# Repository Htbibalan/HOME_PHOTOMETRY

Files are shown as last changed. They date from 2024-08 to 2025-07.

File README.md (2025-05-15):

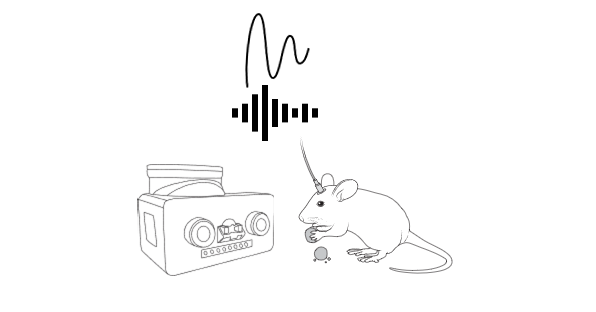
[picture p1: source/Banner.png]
Banner Image


# RTFED_Pi
* RTFED_Pi and associated GUIs is the other version of Clasic ([RTFED](https://github.com/mccutcheonlab/FED_RT/tree/main)) which is an open-source versatile tool for home-cage monitoring of behaviour and fiber photometry recording in mice, this system is developed as a home-cage setup to incorporate [FED3](https://github.com/KravitzLabDevices/FED3/wiki) units with TDT [RZ10](https://www.tdt.com/docs/hardware/rz10-lux-integrated-processor/) photometry system or to capture event-triggered videos of behaviour or to only monitor food intake and other relevant behaviours remotely and online.

# Make sure to flash your FED3 devices with the RTS library provided [here](https://github.com/Htbibalan/FED_RT/tree/main/source/FED3_Library/RTS)

## RbPi Approach
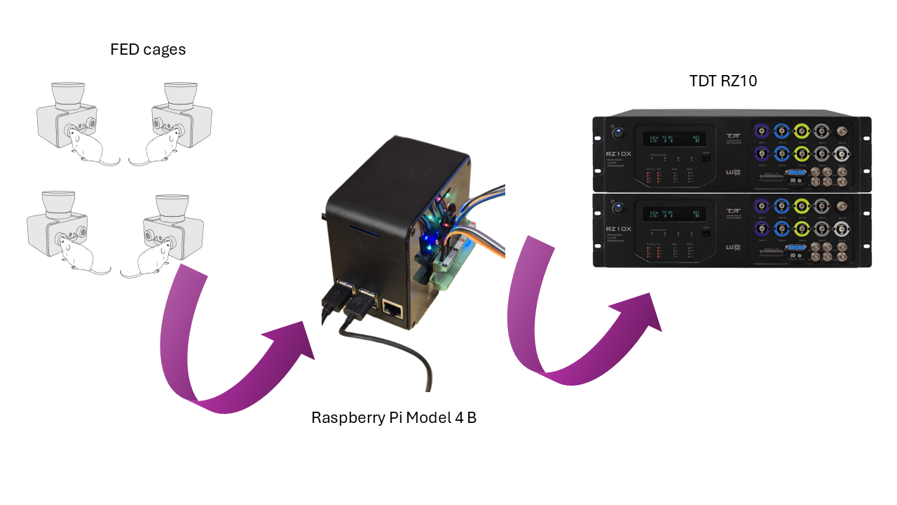
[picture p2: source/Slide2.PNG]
RBPI


RTFED_Pi
RTFED_TOWER

# RTFED(PiOS)
RTFED(PiOS) can be used to remotely monitor the feeding behaviour and other interactions made by mice on FED3, the data is automatically transferred to a Google spreadsheet where you can view it or define alarm notification using the Google Apps Scripts. Using the RTFED you can also change the Mode of your FED3s without the hassle of poking one by one!
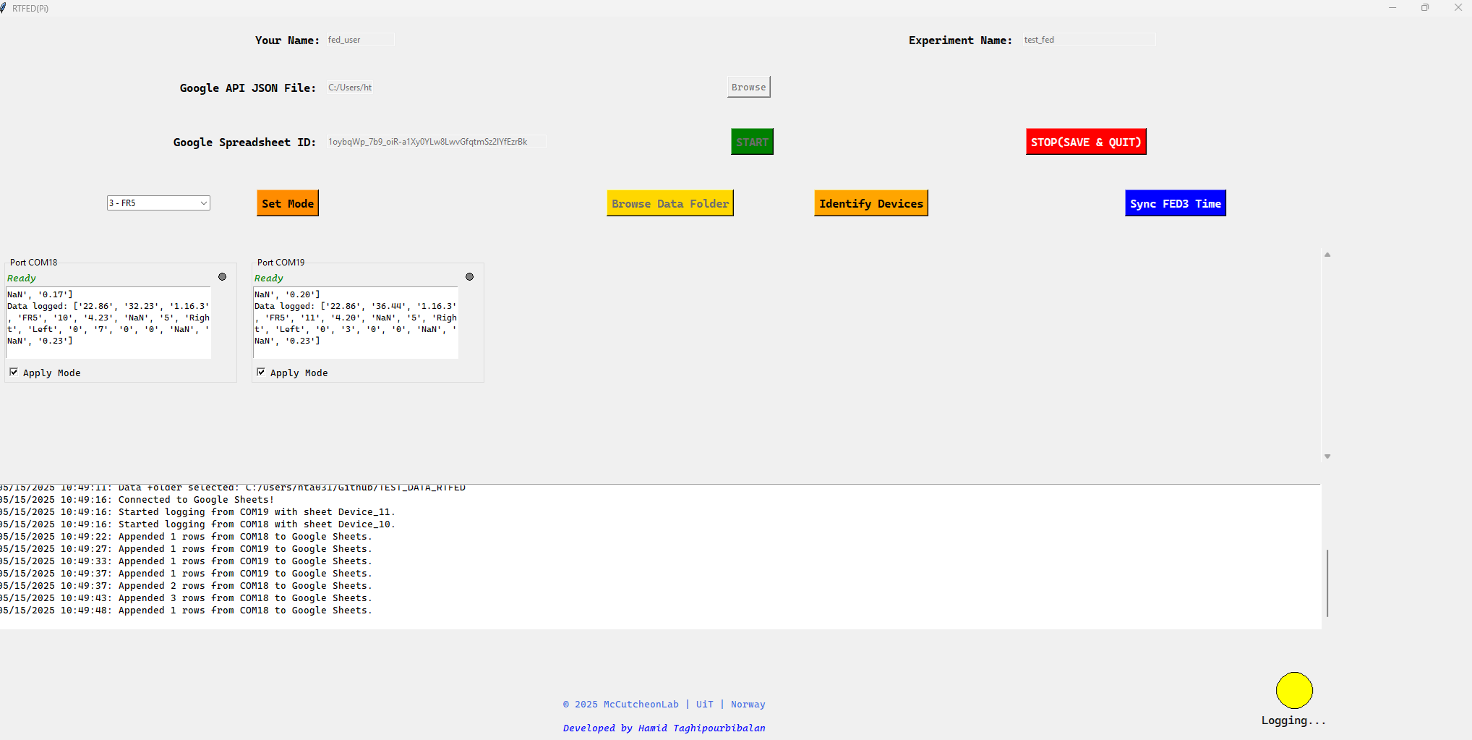
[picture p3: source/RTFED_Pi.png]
RTFED_PiOS


# RTFED(PiCAM)
RTFED(PiCAM) is an additional feature to the basic RTFED where you can enhance your behavioural studies by having event-triggered video recording. Primarily the RTFED(PiCAM) can record videos of mice using common USB cameras after taking Pellets, making Left or Right pokes or a combination of All of these events. Videos are limited to 30 sec length to capture only relevant behaviours while saving storage space, in this configuration, e.g. after taking a pellet, the GUI records the behaviour for 30 sec, if another pellet is taken within this 30 sec, it keeps recording for an extra 30 sec until no more pellet is taken.
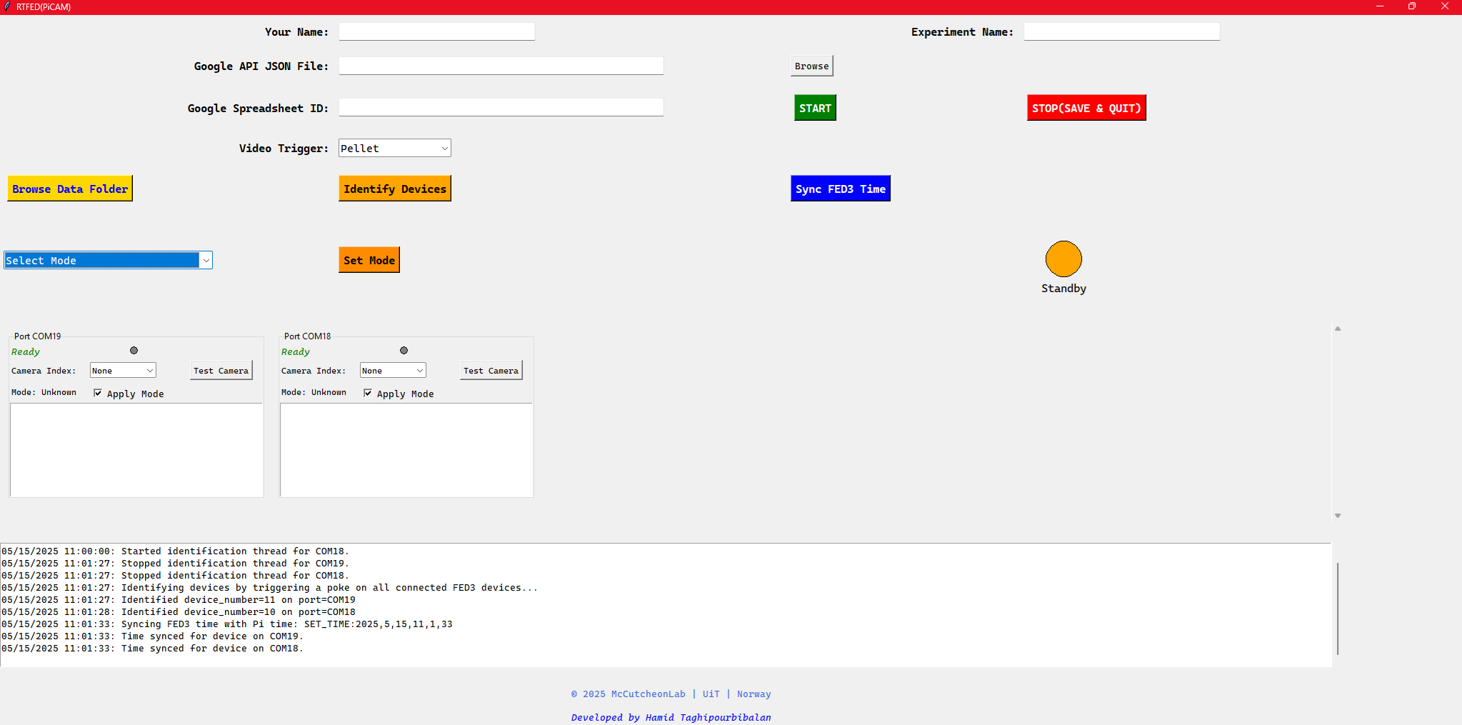
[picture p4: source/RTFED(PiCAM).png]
RTFED_PiCAM


# RTFED(PiTTL)
The TTL station of RTFED logs behavioural events made on FED3 devices and transmit them to the TDT RZ10 processors as TTL pulses. This features enables you to study event-locked signals in your experiments. However the PiTTL version does not send data online to reduce any processing load that might delay the rapid TTL puls transmission.

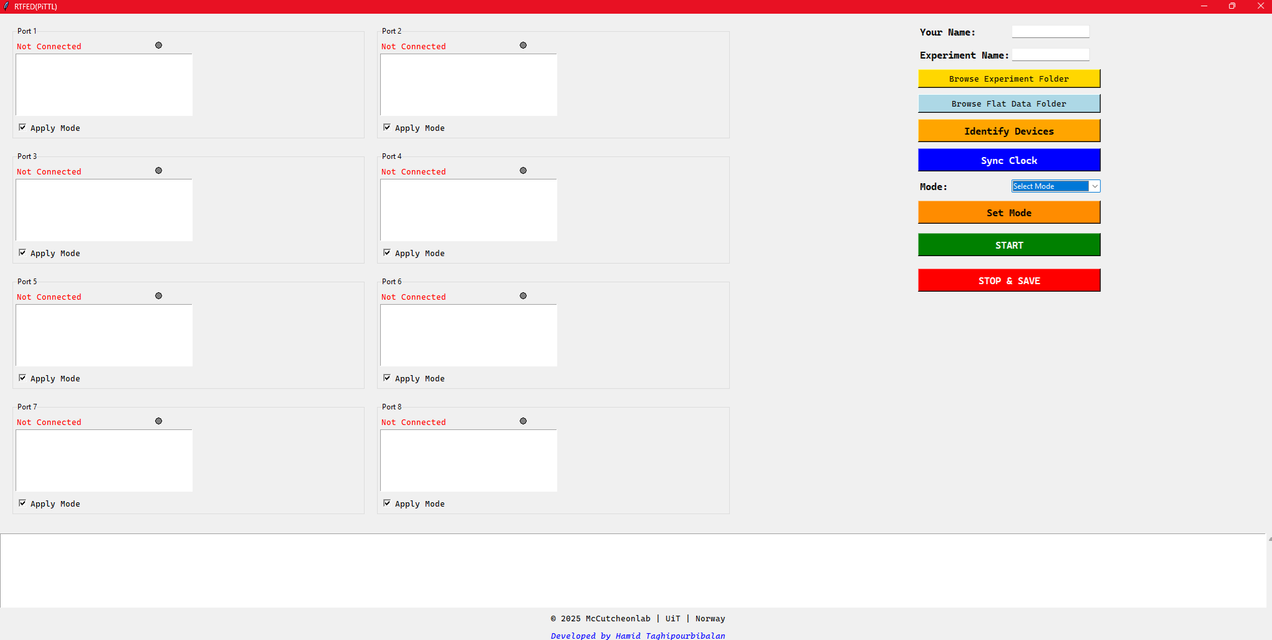
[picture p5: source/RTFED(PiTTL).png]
RTFED_PiTTL


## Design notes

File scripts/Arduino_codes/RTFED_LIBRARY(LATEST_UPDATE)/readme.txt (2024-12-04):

to run RTFED (with or without camera) and the TTL system on raspberry pi, the FEDs should be flashed with these codes

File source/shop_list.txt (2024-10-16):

## The Raspberry Pi 4 Model B - 4 GB RAM
https://www.electrokit.com/en/raspberry-pi-4-model-b/4gb

## A cover case for the board  maybe?(we could 3D print something, but it is already cheap and designing and printing would probably cost more!)
https://www.electrokit.com/en/raspberry-pi-4-inbyggnadslada-rod/vit

## The power adapter for the board
https://www.electrokit.com/en/raspberry-pi-4-stromforsorjning-5v-3a-usb-c-vit

## SD card for the board:
https://www.electrokit.com/en/minneskort-microsdxc-128gb-klass-10-a1

## Jumper wires to connect raspberry pi board to db25 breakoutboard
https://www.elfadistrelec.no/en/jumper-cable-of-40-wires-male-to-female-awg22-velleman-wpa414/p/30260971?ext_cid=shgooaqnono-Shopping-PerformanceMax-CSS&gad_source=1&gclid=CjwKCAjw8rW2BhAgEiwAoRO5rPSryj3k5p8T8V73ak9BMlPEfC4beYDF5v3y66Gtu4eO7EGV2-FF5RoCgv8QAvD_BwE&gclsrc=aw.ds

## DB25 breakout board - connector plug (I am a bit unsure what to choose here)

**Do you think using this one from Amazon makes it easy to map the pins?  - - -instead of using a jumper wire connection to a breakout board and then to TDT.**

#### https://www.amazon.com/JUXINICE-Female-Connector-Provided-Terminals/dp/B0CHNPQBQ8/ref=sr_1_3?crid=2OR78V9CIIFG9&dib=eyJ2IjoiMSJ9.yi8Qg4Rj5wWahTUCXJsKgAnKQk_3SQFYZ_B8QfRRd5V8pHj0V4OxDGAj5KCSfbLMn-YADwfM40hr9cPisJgPzwXafPZrragr_EplipRJSqGdi6IUDoTFnUVk0VAi0_aot9ruiePJBJm4pEvt8D9bhZ1MbMfMwwcu3ZXXE-lrJochcbtGk-mPSx4gX2LDumzK5paAzaQJFuXtPuggM7bJzDdVVN1RYlLLHZg9duVD96s.VZK6kxQxmFYSIs7IfyqwNdEzwP57swXu5cxePmbuzlM&dib_tag=se&keywords=db25%2Bpigtail%2Bfemale%2Bjumper%2Bwire%2Bon%2Bend&qid=1724755007&sprefix=db25%2Bpigtail%2Bfemale%2Bjumper%2Bwire%2Bon%2Ben%2Caps%2C204&sr=8-3&th=1

#### https://czh-labs.com/products/czh-labs-slim-right-angle-dsub-db25-male-header-breakout-board-module-d-sub-231?gad_source=1&gclid=CjwKCAjw8rW2BhAgEiwAoRO5rEic1w67dlyraS9dUXNrp32Dhq9PTFB_XoJzjpuoE9zxFm3M3ATWWRoCE30QAvD_BwE

#### https://www.multicom.no/delock-seriell-adapter-db-25-til/cat-p/c/p5398359?gad_source=1&gclid=CjwKCAjw8rW2BhAgEiwAoRO5rKDj3SsBziStjbM7XgD4G3ZDbnNtTQQtALRzAGIcXfvrEBEA31QwJhoCIz0QAvD_BwE

## micro-USB extension
When mounted, the usb port on feather board of FEDs is very badly accessible,this tiny extension can be plugged in and folded back inside the FED housing -- - so the user can easily plug the USB cable on and off

https://www.amazon.com/Uogw-Micro-USB-Extension-Compatible-Extender/dp/B0CLNST44W/ref=sr_1_12_sspa?crid=2T2GL28DFSUQF&dib=eyJ2IjoiMSJ9.ToT3-_PpHgo8qtZdqoQMA_RmyXm6rntiebAVAt7THINzPbDIxeCftpZySoyK1GaJeZY26zIsTFYda32_0IthTOMxalG1sVhi6l7dpbQTZtIAAegbQhmTqVs8Re8zaWFydS_tD66FhC2EADfzfWHkswVANtIlt0KJgT7VXEkySAhnAKVyMKRxunJ3VUaQDT3ZaAcAWanG9JjlNHgFYxLHJ7A2aLwAGYZ1YsdB2rNlqzk.O1Yd72mzAjQylSQsHVLrKwEAeE-LObh2ErCST5r62MY&dib_tag=se&keywords=micro+usb+extension&qid=1724755350&sprefix=micro+usb+extensio%2Caps%2C215&sr=8-12-spons&sp_csd=d2lkZ2V0TmFtZT1zcF9tdGY&psc=1

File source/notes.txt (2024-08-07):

Andrew Hardaway method to sync FED with photometry
https://hackaday.io/project/106885-feeding-experimentation-device-3-fed3/log/162040-interfacing-fed3-with-bonsai

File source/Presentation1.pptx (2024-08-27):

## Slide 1

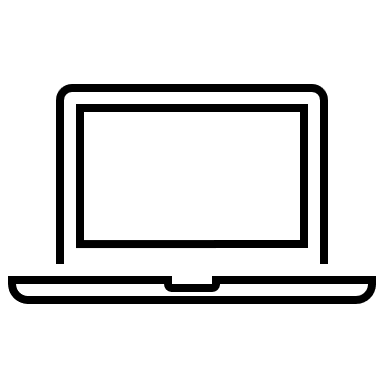
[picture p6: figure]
Laptop outline

Central computer

FED cages

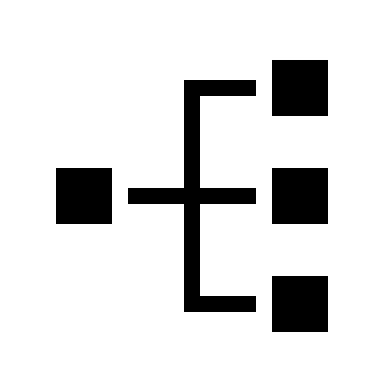
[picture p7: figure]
Network diagram with solid fill
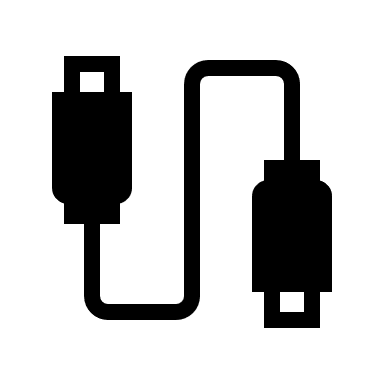
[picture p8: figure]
USB with solid fill
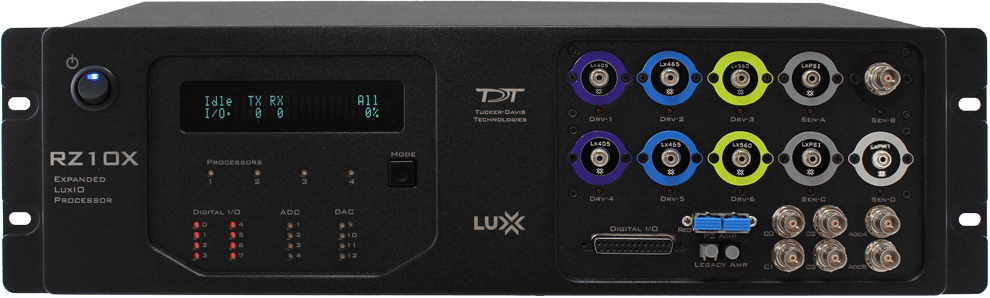
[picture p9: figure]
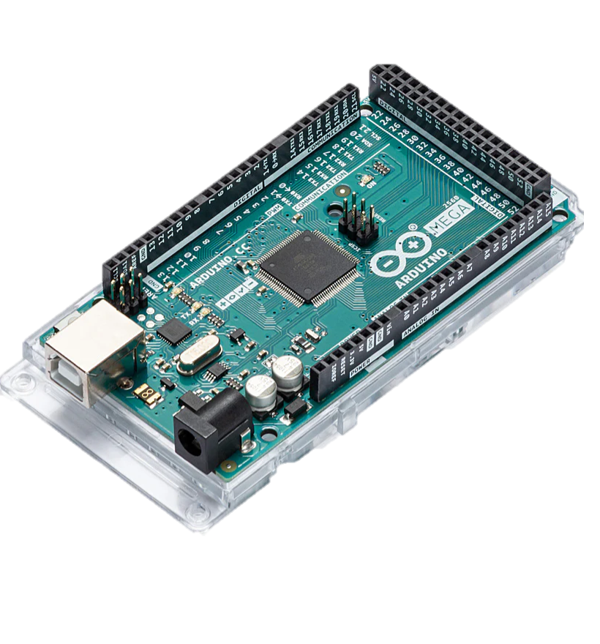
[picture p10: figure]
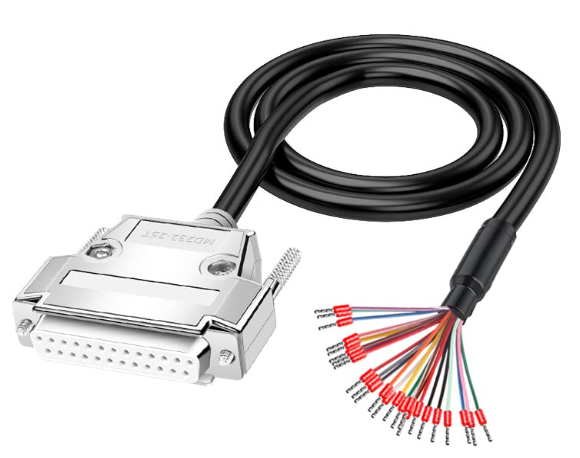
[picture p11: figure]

Arduino Mega

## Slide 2

Raspberry Pi Model 4 B

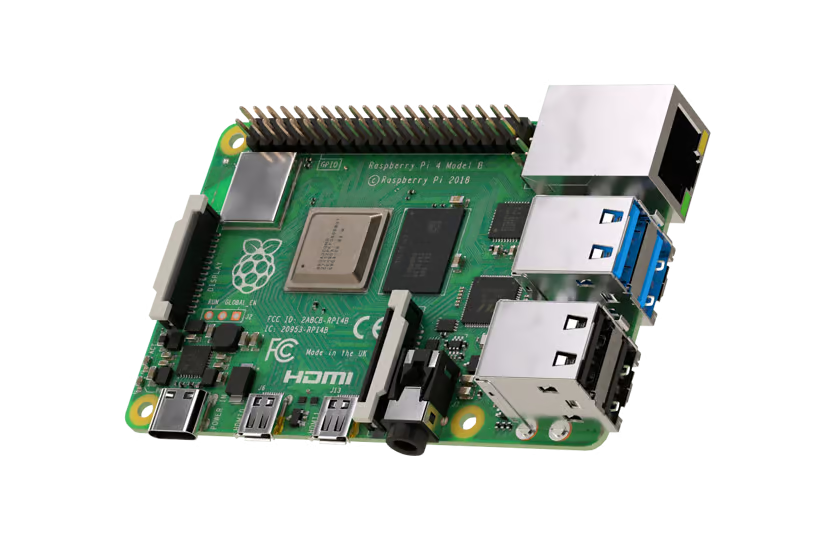
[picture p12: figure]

FED cages

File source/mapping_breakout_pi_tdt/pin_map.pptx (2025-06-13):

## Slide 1

Db25 breakout to TDT

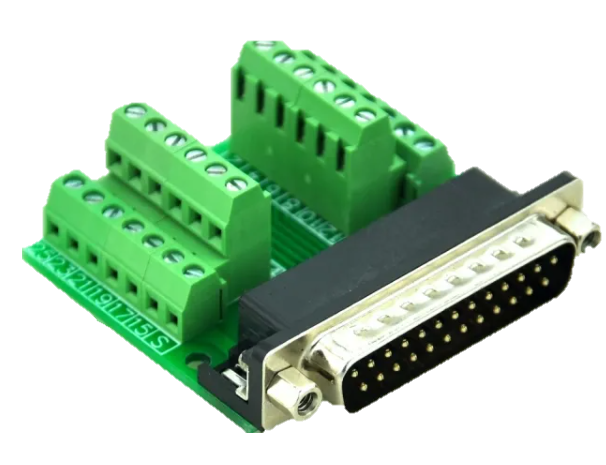
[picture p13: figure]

Port 3/4
Db25 Pin Jumper colour
1 White Right 5
14 Gray Left 0
2 Black Pellet 6
15 Red Right 19
3 Brown Left 13
16 Orange Pellet 26
5 Purple Ground

Raspberry Pi GPIO pinout

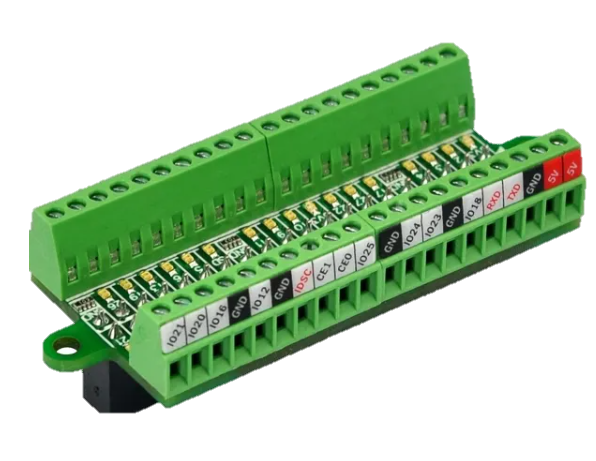
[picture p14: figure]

gpio_pins_per_device = {
'Port 1': {"LeftPoke": 17, "RightPoke": 27, "Pellet": 22},
'Port 2': {"LeftPoke": 10, "RightPoke": 9, "Pellet": 11},
'Port 3': {"LeftPoke": 0, "RightPoke": 5, "Pellet": 6},
'Port 4': {"LeftPoke": 13, "RightPoke": 19, "Pellet": 26},
'Port 5': {"LeftPoke": 14, "RightPoke": 15, "Pellet": 18},
'Port 6': {"LeftPoke": 23, "RightPoke": 24, "Pellet": 25},
'Port 7': {"LeftPoke": 8, "RightPoke": 7, "Pellet": 1},
'Port 8': {"LeftPoke": 12, "RightPoke": 16, "Pellet": 20},
}

Port 1/2
Db25 Pin Jumper colour
1 White Right 27
14 Gray Left 17
2 Black Pellet 22
15 Green Right 9
3 Yellow Left 10
16 Blue Pellet 11
5 Purple Ground

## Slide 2

Raspberry Pi GPIO pinout

gpio_pins_per_device = {
'Port 1': {"LeftPoke": 17, "RightPoke": 27, "Pellet": 22},
'Port 2': {"LeftPoke": 10, "RightPoke": 9, "Pellet": 11},
'Port 3': {"LeftPoke": 0, "RightPoke": 5, "Pellet": 6},
'Port 4': {"LeftPoke": 13, "RightPoke": 19, "Pellet": 26},
'Port 5': {"LeftPoke": 14, "RightPoke": 15, "Pellet": 18},
'Port 6': {"LeftPoke": 23, "RightPoke": 24, "Pellet": 25},
'Port 7': {"LeftPoke": 8, "RightPoke": 7, "Pellet": 1},
'Port 8': {"LeftPoke": 12, "RightPoke": 16, "Pellet": 20},
}

Db25 breakout to TDT

Port 1/2
Db25 Pin Pi pin
1 Right 27
14 Left 17
2 Pellet 22
15 Right 9
3 Left 10
16 Pellet 11
5 Ground

Port 3/4
Db25 Pin Pi pin
1 Right 5
14 Left 0
2 Pellet 6
15 Right 19
3 Left 13
16 Pellet 26
5 Ground

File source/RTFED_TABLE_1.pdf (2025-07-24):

Component | Quantity | Cost/unit (USD) | PiTTL | PiCAM | Basic
Raspberry Pi 4 Model B 4 GB | 1 | 62 | ✓ | ✓
Power supply 15W USB-C | 1 | 9 | ✓ | ✓
Memory card microSD 128 GB Class 10 A1 | 1 | 15 | ✓ | ✓
Raspberry Pi 4 B Tower Case | 1 | 30 | ✓ | ✓
DB25 Male Header Breakout Board | 2 | 12 | ✓
Ultra-small RPi GPIO LED Breakout | 1 | 19 | ✓
Jumper wires Male-Male | 1 | 3.5 | ✓
Arducam 1080P Day/Night Vision USB Camera | As needed | 34 | | ✓
USB Camera mount | As needed | – | | ✓
Powered USB hub | As needed | 20 | ✓ | ✓ | ✓
Long USB-A to Micro-B cables | As needed | 7.5 | ✓ | ✓ | ✓
MicroHDMI cable | 1 | 8 | ✓ | ✓
Bluetooth keyboard-touchpad | 1 | 40 | ✓ | ✓
Optional: DB25 extension cable | 2 | 30 | ✓
FED3 (Fully assembled) | As needed | 475 | ✓ | ✓ | ✓

1

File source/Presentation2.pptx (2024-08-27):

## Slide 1

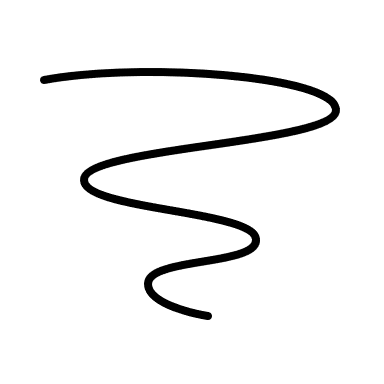
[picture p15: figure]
Squiggle outline
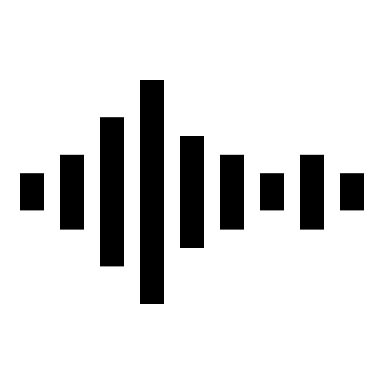
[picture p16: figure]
Voice with solid fill
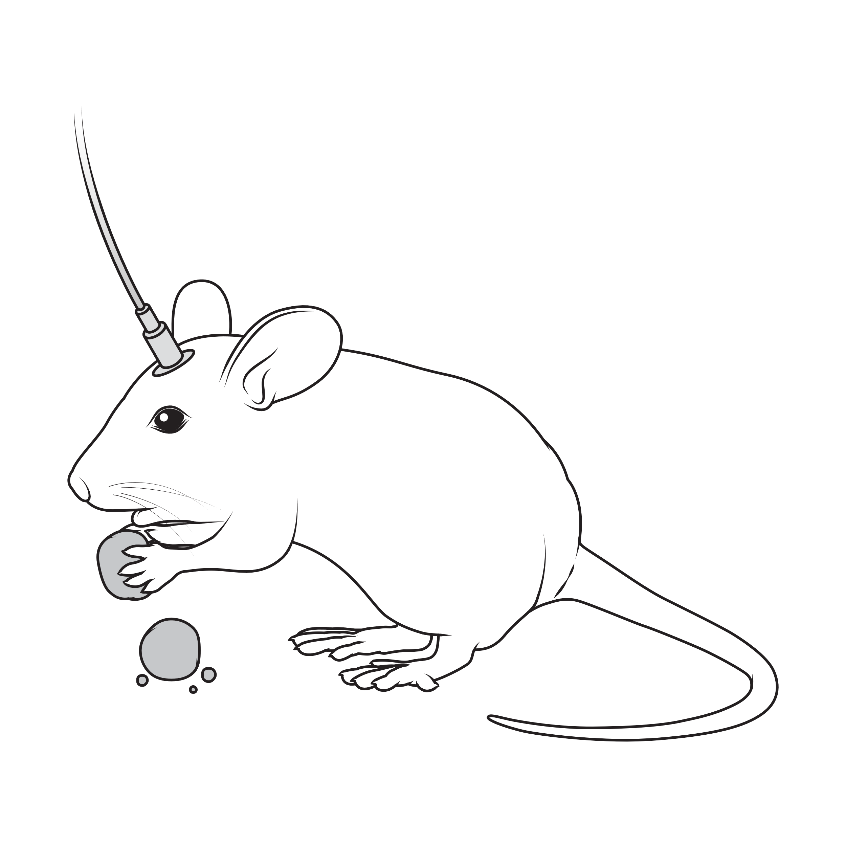
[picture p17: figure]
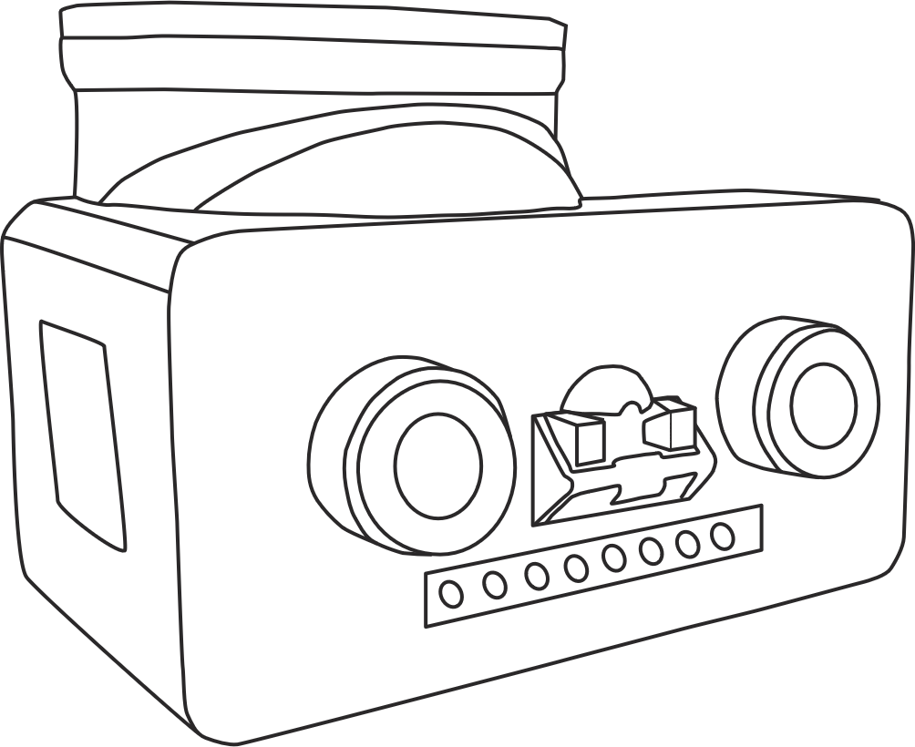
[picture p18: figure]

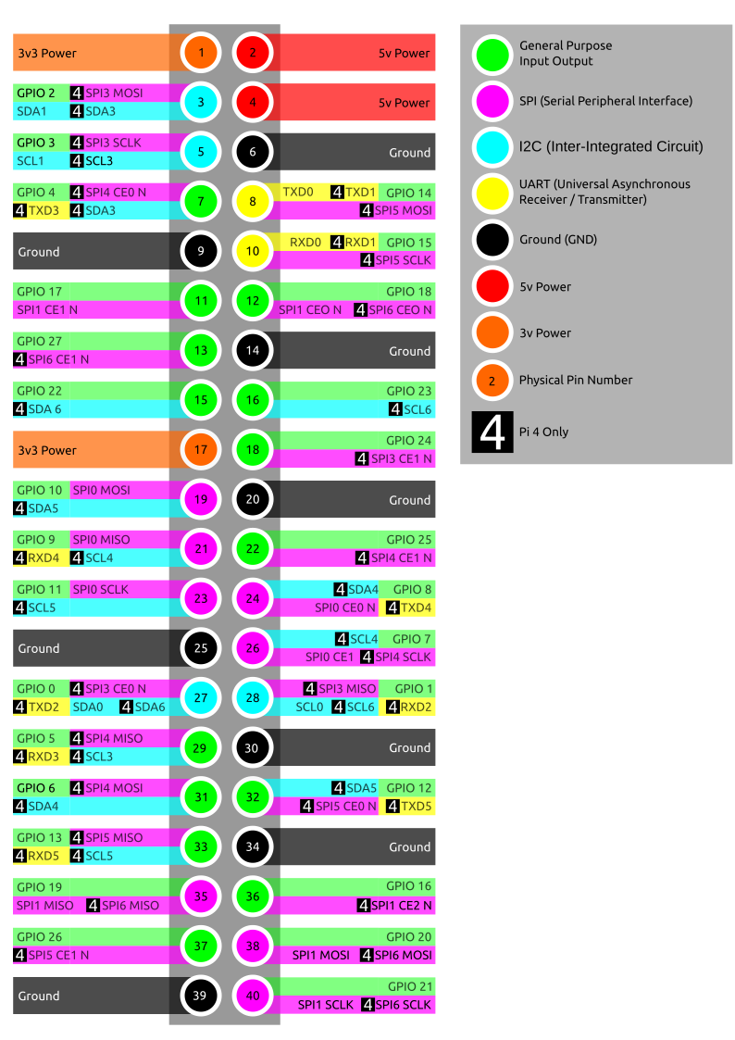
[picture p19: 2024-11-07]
source/PINOUT_rbpi4.png

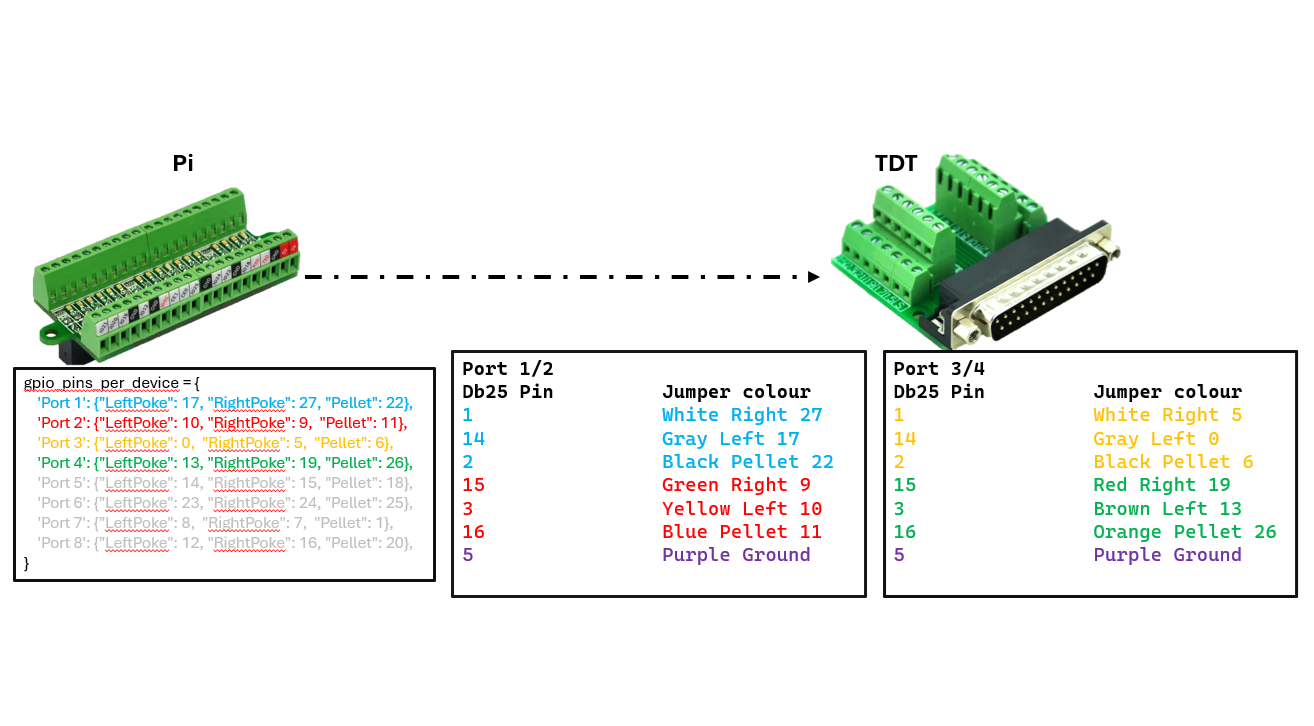
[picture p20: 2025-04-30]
source/mapping_breakout_pi_tdt/pin_map.png

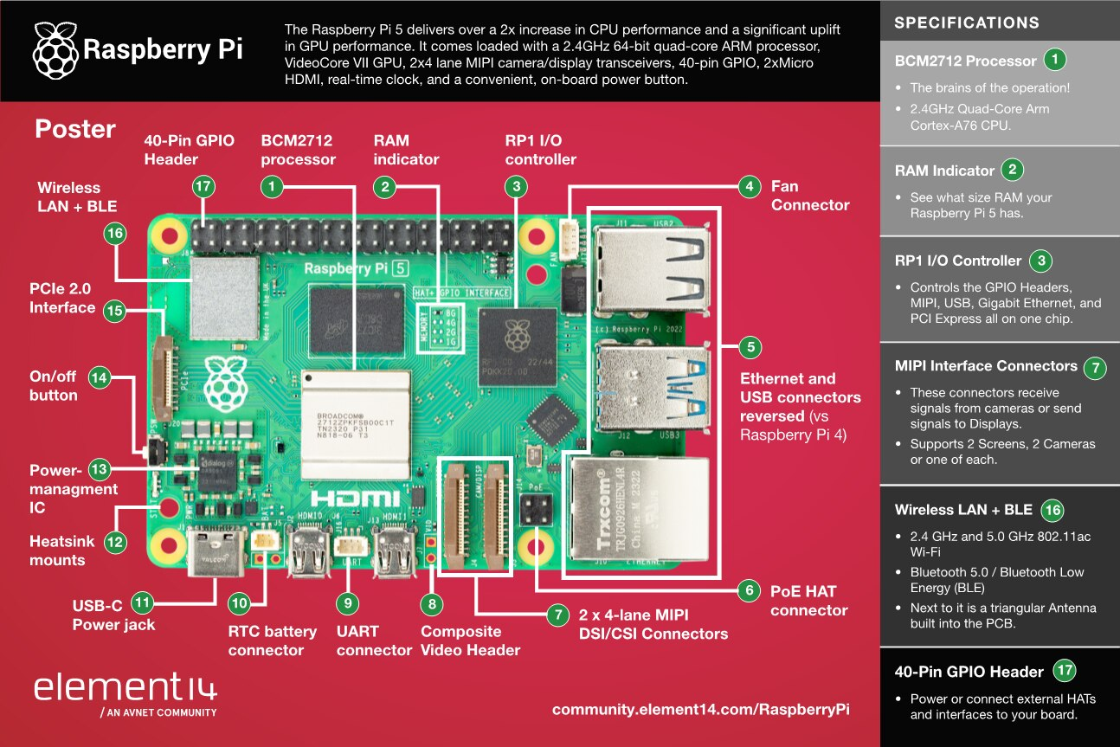
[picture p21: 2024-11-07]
source/otep3xr6.png

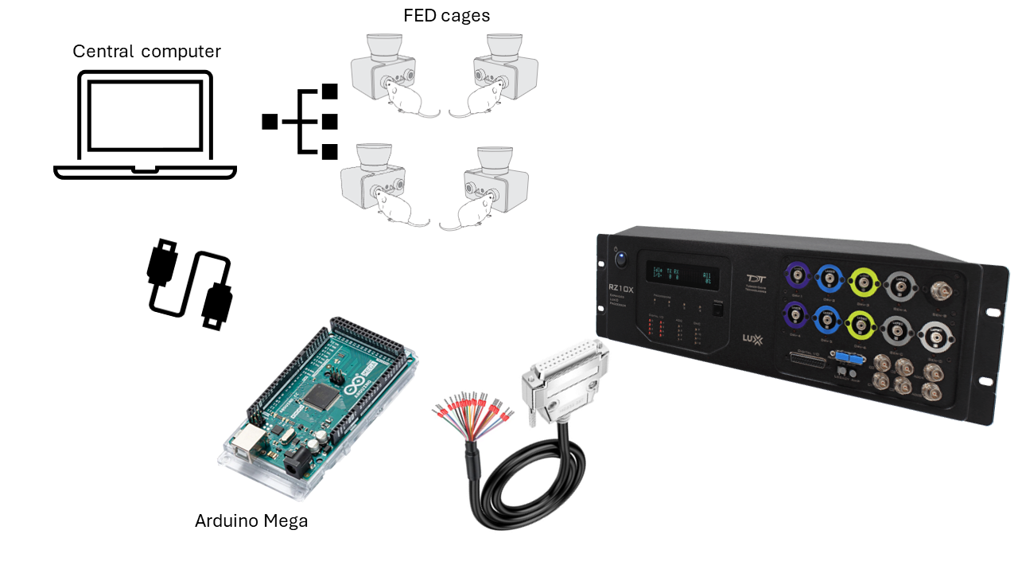
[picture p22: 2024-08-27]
source/Slide1.PNG

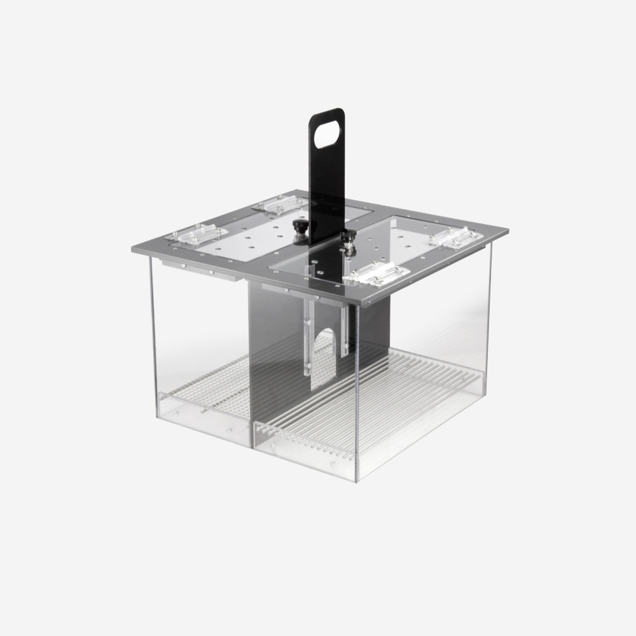
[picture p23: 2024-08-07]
source/hinge_medbox.jpg

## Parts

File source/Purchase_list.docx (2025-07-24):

Component | Quantity | ~ Cost/unit (USD) | Suggested source | Comments
Raspberry Pi 4 Model B 4 GB | 1 | 62 | Amazon (https://www.amazon.com/Raspberry-Pi-RPI4-MODBP-4GB-Model-4GB/dp/B09TTNF8BT) | Only for photometry and video recording
Power supply 15W USB-C | 1 | 9 | Amazon (https://www.amazon.com/Raspberry-Supply-iUniker-Switch-Listed/dp/B097P2NLVH) | Only for photometry and video recording
Memory card microSD 128 GB Class 10 A 1 | 1 | 15 | Amazon (https://www.amazon.com/SanDisk-128GB-microSDXC-Memory-Adapter/dp/B0B7NTY2S6) | Only for photometry and video recording
Raspberry Pi 4 B Tower Case | 1 | 30 | Amazon (https://www.amazon.com/ElectroCookie-Raspberry-Aluminum-Cooling-Changing/dp/B09QG349ZL) | Only for photometry and video recording
DB25 Male Header Breakout Board | 2 | 12 | CZH-LABS (https://czh-labs.com/products/czh-labs-slim-right-angle-dsub-db25-male-header-breakout-board-module-d-sub-231) | Only for photometry
Ultra-small RPi GPIO Status LED & Terminal Block Breakout Board | 1 | 19 | CZH-LABS (https://czh-labs.com/products/ultra-small-rpi-gpio-status-led-terminal-block-breakout-board-module-for-raspberry-pi) | Only for photometry
Jumper wires Male-Male | 1 | 3.5 | Arduino (https://store-usa.arduino.cc/products/40-colored-male-male-jumper-wires) | Only for photometry
Arducam 1080P Day/Night Vision USB Camera | As needed | 34 | ArduCam (https://www.arducam.com/arducam-1080p-day-night-vision-usb-camera-2mp-infrared-webcam-with-automatic-ir-cut-switching-and-ir-leds.html) | If video recording needed
USB Camera mount | As needed | - | TinkerCAD (https://www.tinkercad.com/things/21BWhLxcOKk-cameramount) | If video recording needed
Powered USB hub | 1 | 20 | Amazon (https://www.amazon.com/FEMORO-Charging-Splitter-Individual-Switches/dp/B0CG8YR4W7) | For more than 4 FEDs
Long USB-A to Micro-B cables | As needed | 7.5 | Amazon (https://www.amazon.com/dp/B07232M876/ref=twister_B072FHJVT2?_encoding=UTF8&th=1)
MicroHDMI cable | 1 | 8 | Amazon (https://www.amazon.com/oldboytech-Adapter-Compatible-Raspberry-Capture/dp/B08C2PVP7J?sp_csd=d2lkZ2V0TmFtZT1zcF9hdGY) | Only for photometry and video recording
Bluetooth keyboard-touchpad | 1 | 40 | Amazon (https://www.amazon.com/Arteck-Universal-7-Colors-Bluetooth-TV-Connected/dp/B09KLPJQPD?sp_csd=d2lkZ2V0TmFtZT1zcF9hdGY) | Only for photometry and video recording
Optional: Male to Female db25 extension cable | 2 | | | Only for photometry
FED3

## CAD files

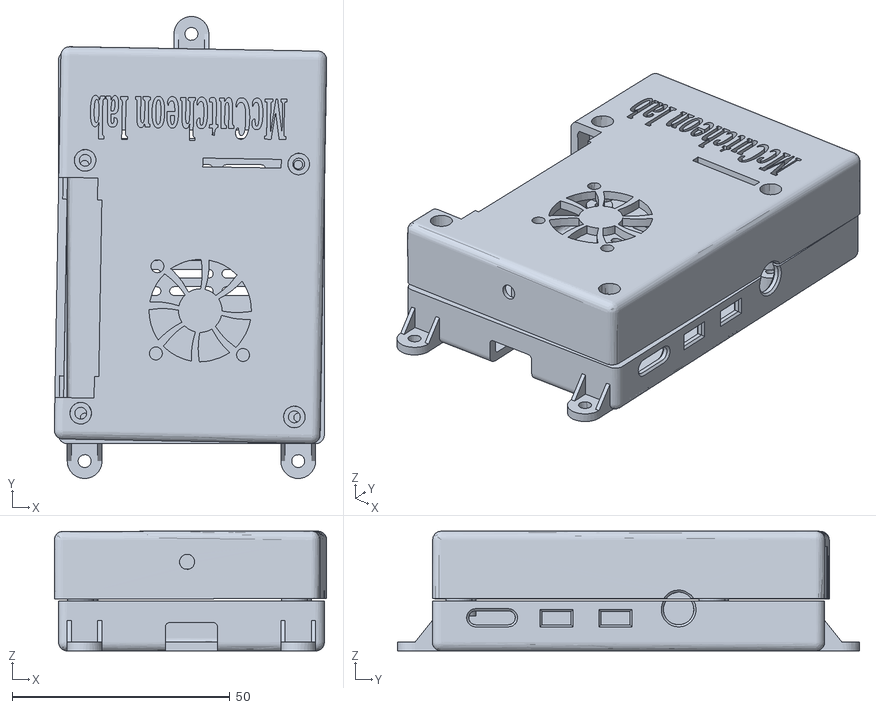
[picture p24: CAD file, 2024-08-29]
source/3D_Model_RbPi/V2/RbPi_V1_whole.stl
62.5 x 106.0 x 27.5

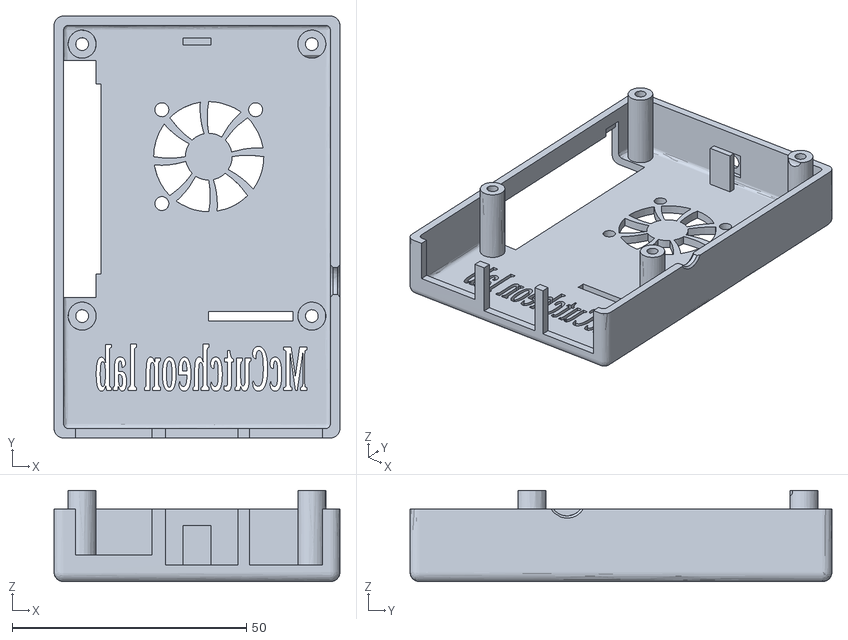
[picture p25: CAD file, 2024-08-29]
source/3D_Model_RbPi/V2/RbPI_V3_Front.stl
61.0 x 90.0 x 19.4

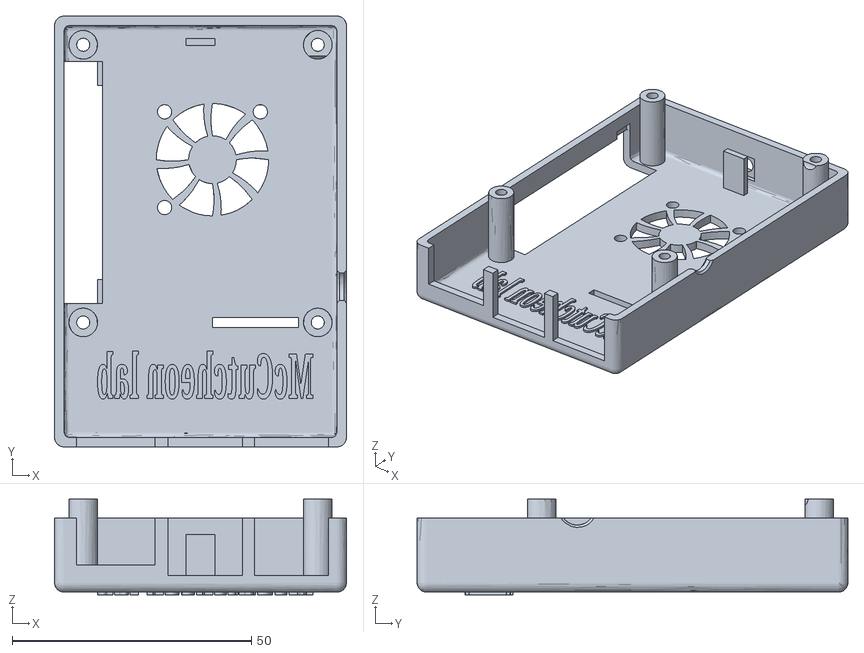
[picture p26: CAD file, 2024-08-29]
source/3D_Model_RbPi/V2/RbPI_V2_Front.stl
61.0 x 90.0 x 20.0

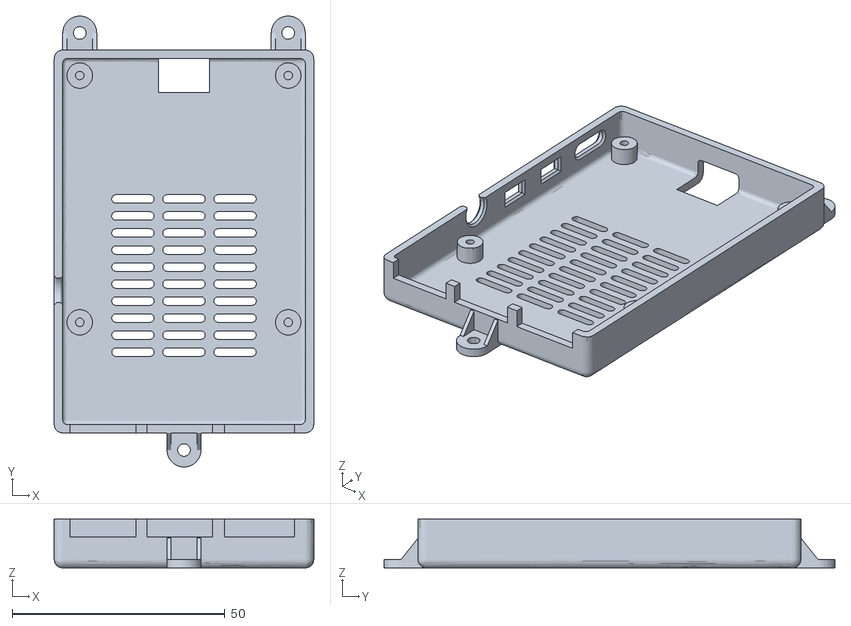
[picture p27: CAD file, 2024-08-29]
source/3D_Model_RbPi/V2/RbPi_V3_Back.stl
61.0 x 106.0 x 11.5

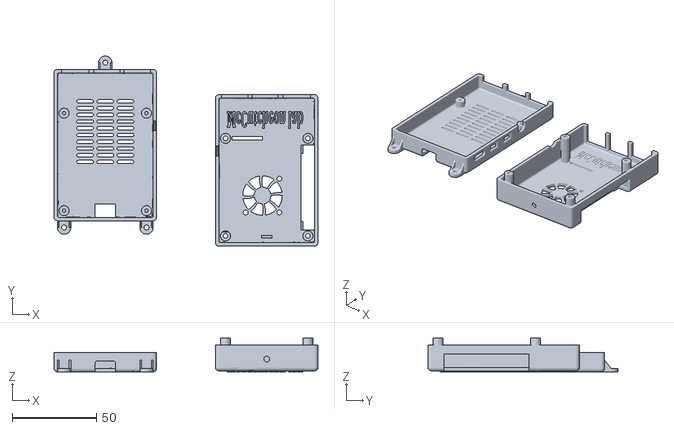
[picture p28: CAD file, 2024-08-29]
source/3D_Model_RbPi/V2/RbPi_V2.stl
157.0 x 113.0 x 20.0

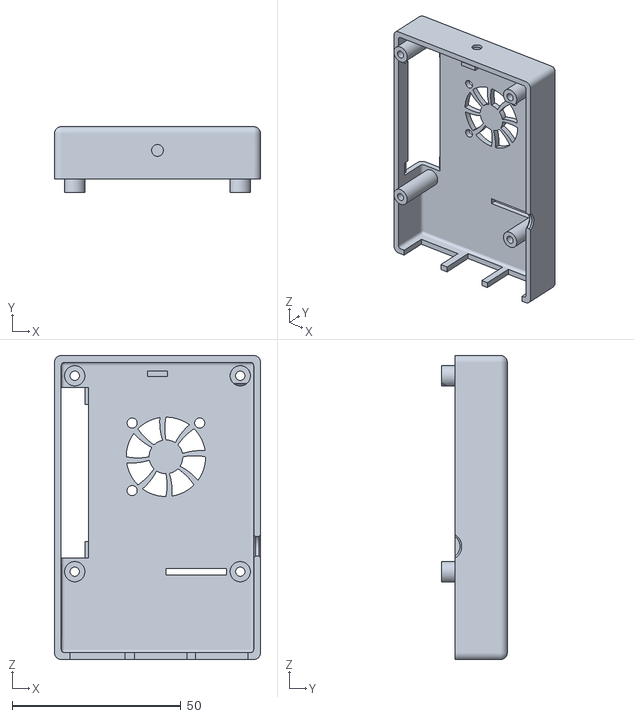
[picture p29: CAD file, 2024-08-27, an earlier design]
source/3D_Model_RbPi/V1/top_V1.stl
61.0 x 19.4 x 90.0

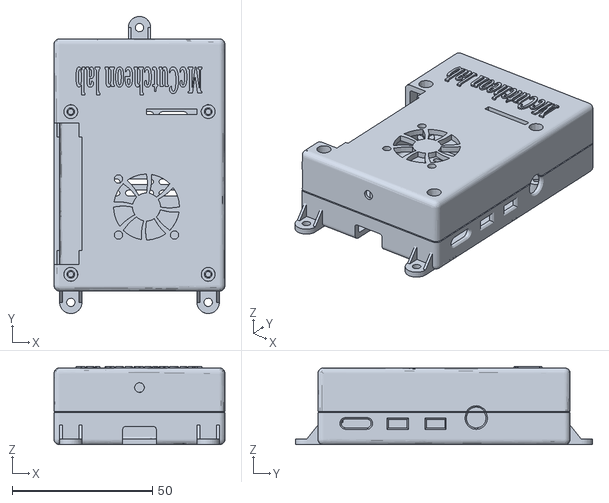
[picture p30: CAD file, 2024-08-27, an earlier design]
source/3D_Model_RbPi/V1/RbPi_V1.stl
61.0 x 106.0 x 28.0

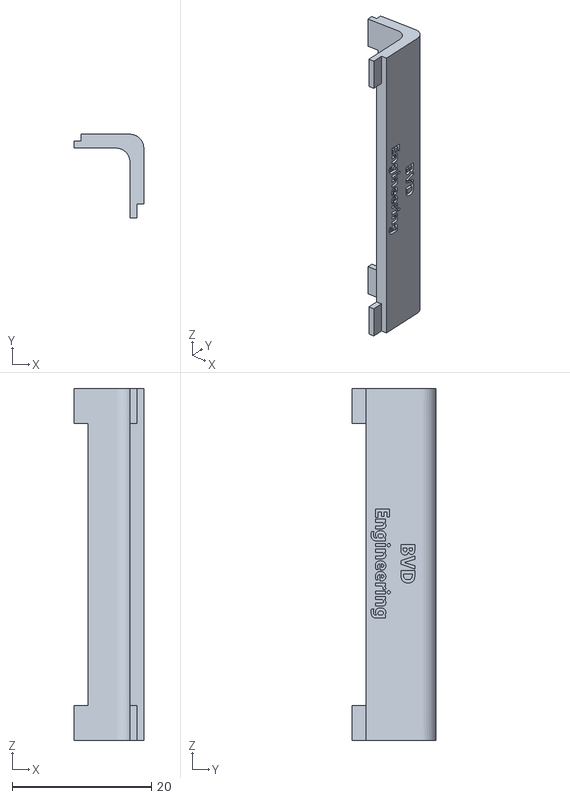
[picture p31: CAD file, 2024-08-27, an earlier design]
source/3D_Model_RbPi/V1/cover_V1.stl
10.0 x 12.0 x 50.5

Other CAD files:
source/3D_Model_RbPi/V1/bottom_V1.stl

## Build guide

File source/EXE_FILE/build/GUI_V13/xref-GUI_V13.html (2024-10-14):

# modulegraph cross reference for GUI_V13.py, pyi_rth__tkinter.py, pyi_rth_inspect.py

GUI_V13.py Script

imports: RPi.GPIO • _collections_abc • _weakrefset • abc • codecs • collections • collections.abc • copyreg • csv • datetime • encodings • encodings.aliases • encodings.ascii • encodings.base64_codec • encodings.big5 • encodings.big5hkscs • encodings.bz2_codec • encodings.charmap • encodings.cp037 • encodings.cp1006 • encodings.cp1026 • encodings.cp1125 • encodings.cp1140 • encodings.cp1250 • encodings.cp1251 • encodings.cp1252 • encodings.cp1253 • encodings.cp1254 • encodings.cp1255 • encodings.cp1256 • encodings.cp1257 • encodings.cp1258 • encodings.cp273 • encodings.cp424 • encodings.cp437 • encodings.cp500 • encodings.cp720 • encodings.cp737 • encodings.cp775 • encodings.cp850 • encodings.cp852 • encodings.cp855 • encodings.cp856 • encodings.cp857 • encodings.cp858 • encodings.cp860 • encodings.cp861 • encodings.cp862 • encodings.cp863 • encodings.cp864 • encodings.cp865 • encodings.cp866 • encodings.cp869 • encodings.cp874 • encodings.cp875 • encodings.cp932 • encodings.cp949 • encodings.cp950 • encodings.euc_jis_2004 • encodings.euc_jisx0213 • encodings.euc_jp • encodings.euc_kr • encodings.gb18030 • encodings.gb2312 • encodings.gbk • encodings.hex_codec • encodings.hp_roman8 • encodings.hz • encodings.idna • encodings.iso2022_jp • encodings.iso2022_jp_1 • encodings.iso2022_jp_2 • encodings.iso2022_jp_2004 • encodings.iso2022_jp_3 • encodings.iso2022_jp_ext • encodings.iso2022_kr • encodings.iso8859_1 • encodings.iso8859_10 • encodings.iso8859_11 • encodings.iso8859_13 • encodings.iso8859_14 • encodings.iso8859_15 • encodings.iso8859_16 • encodings.iso8859_2 • encodings.iso8859_3 • encodings.iso8859_4 • encodings.iso8859_5 • encodings.iso8859_6 • encodings.iso8859_7 • encodings.iso8859_8 • encodings.iso8859_9 • encodings.johab • encodings.koi8_r • encodings.koi8_t • encodings.koi8_u • encodings.kz1048 • encodings.latin_1 • encodings.mac_arabic • encodings.mac_croatian • encodings.mac_cyrillic • encodings.mac_farsi • encodings.mac_greek • encodings.mac_iceland • encodings.mac_latin2 • encodings.mac_roman • encodings.mac_romanian • encodings.mac_turkish • encodings.mbcs • encodings.oem • encodings.palmos • encodings.ptcp154 • encodings.punycode • encodings.quopri_codec • encodings.raw_unicode_escape • encodings.rot_13 • encodings.shift_jis • encodings.shift_jis_2004 • encodings.shift_jisx0213 • encodings.tis_620 • encodings.undefined • encodings.unicode_escape • encodings.utf_16 • encodings.utf_16_be • encodings.utf_16_le • encodings.utf_32 • encodings.utf_32_be • encodings.utf_32_le • encodings.utf_7 • encodings.utf_8 • encodings.utf_8_sig • encodings.uu_codec • encodings.zlib_codec • enum • functools • genericpath • heapq • io • keyword • linecache • locale • logging • ntpath • operator • os • posixpath • pyi_rth__tkinter.py • pyi_rth_inspect.py • queue • re • re._casefix • re._compiler • re._constants • re._parser • reprlib • serial • sre_compile • sre_constants • sre_parse • stat • sys • threading • time • tkinter • tkinter.filedialog • tkinter.font • tkinter.ttk • traceback • types • warnings • weakref

pyi_rth__tkinter.py Script

imports: os • sys

imported by: GUI_V13.py

pyi_rth_inspect.py Script

imports: inspect • os • sys

imported by: GUI_V13.py

'System.IO' MissingModule

imported by: serial.serialcli

'org.python' MissingModule

imported by: copy

RPi Package

imported by: RPi.GPIO • RPi._GPIO

RPi.GPIO Package

imports: RPi • RPi._GPIO

imported by: GUI_V13.py

RPi._GPIO /home/hpfed/HOMEPHOTOFED/lib/python3.11/site-packages/RPi/_GPIO.cpython-311-aarch64-linux-gnu.so

imports: RPi

imported by: RPi.GPIO

System MissingModule

imported by: serial.serialcli

__future__ SourceModule

imported by: serial • serial.serialcli • serial.serialjava • serial.serialposix • serial.serialutil • serial.serialwin32 • serial.win32

_abc (builtin module)

imported by: abc

_ast (builtin module)

imported by: ast

_bisect (builtin module)

imported by: bisect

_blake2 (builtin module)

imported by: hashlib

_bz2 /usr/lib/python3.11/lib-dynload/_bz2.cpython-311-aarch64-linux-gnu.so

imported by: bz2

_codecs (builtin module)

imported by: codecs

_codecs_cn /usr/lib/python3.11/lib-dynload/_codecs_cn.cpython-311-aarch64-linux-gnu.so

imported by: encodings.gb18030 • encodings.gb2312 • encodings.gbk • encodings.hz

_codecs_hk /usr/lib/python3.11/lib-dynload/_codecs_hk.cpython-311-aarch64-linux-gnu.so

imported by: encodings.big5hkscs

_codecs_iso2022 /usr/lib/python3.11/lib-dynload/_codecs_iso2022.cpython-311-aarch64-linux-gnu.so

imported by: encodings.iso2022_jp • encodings.iso2022_jp_1 • encodings.iso2022_jp_2 • encodings.iso2022_jp_2004 • encodings.iso2022_jp_3 • encodings.iso2022_jp_ext • encodings.iso2022_kr

_codecs_jp /usr/lib/python3.11/lib-dynload/_codecs_jp.cpython-311-aarch64-linux-gnu.so

imported by: encodings.cp932 • encodings.euc_jis_2004 • encodings.euc_jisx0213 • encodings.euc_jp • encodings.shift_jis • encodings.shift_jis_2004 • encodings.shift_jisx0213

_codecs_kr /usr/lib/python3.11/lib-dynload/_codecs_kr.cpython-311-aarch64-linux-gnu.so

imported by: encodings.cp949 • encodings.euc_kr • encodings.johab

_codecs_tw /usr/lib/python3.11/lib-dynload/_codecs_tw.cpython-311-aarch64-linux-gnu.so

imported by: encodings.big5 • encodings.cp950

_collections (builtin module)

imported by: collections • threading

_collections_abc SourceModule

imports: abc • sys

imported by: GUI_V13.py • collections • collections.abc • contextlib • locale • os • pathlib • random • types • weakref

_compat_pickle SourceModule

imported by: _pickle • pickle

_compression SourceModule

imports: io • sys

imported by: bz2 • gzip • lzma

_contextvars /usr/lib/python3.11/lib-dynload/_contextvars.cpython-311-aarch64-linux-gnu.so

imported by: contextvars

_csv (builtin module)

imported by: csv

_ctypes /usr/lib/python3.11/lib-dynload/_ctypes.cpython-311-aarch64-linux-gnu.so

imported by: ctypes

_datetime (builtin module)

imports: _strptime • time

imported by: datetime

_decimal /usr/lib/python3.11/lib-dynload/_decimal.cpython-311-aarch64-linux-gnu.so

imported by: decimal

_frozen_importlib ExcludedModule

imported by: importlib • importlib.abc

_frozen_importlib_external MissingModule

imported by: importlib • importlib._bootstrap • importlib.abc

_functools (builtin module)

imported by: functools

_hashlib /usr/lib/python3.11/lib-dynload/_hashlib.cpython-311-aarch64-linux-gnu.so

imported by: hashlib

_heapq (builtin module)

imported by: heapq

_imp (builtin module)

imported by: importlib • importlib._bootstrap_external • importlib.util

_io (builtin module)

imported by: importlib._bootstrap_external • io

_locale (builtin module)

imported by: locale

_lzma /usr/lib/python3.11/lib-dynload/_lzma.cpython-311-aarch64-linux-gnu.so

imported by: lzma

_md5 (builtin module)

imported by: hashlib

_multibytecodec /usr/lib/python3.11/lib-dynload/_multibytecodec.cpython-311-aarch64-linux-gnu.so

imported by: encodings.big5 • encodings.big5hkscs • encodings.cp932 • encodings.cp949 • encodings.cp950 • encodings.euc_jis_2004 • encodings.euc_jisx0213 • encodings.euc_jp • encodings.euc_kr • encodings.gb18030 • encodings.gb2312 • encodings.gbk • encodings.hz • encodings.iso2022_jp • encodings.iso2022_jp_1 • encodings.iso2022_jp_2 • encodings.iso2022_jp_2004 • encodings.iso2022_jp_3 • encodings.iso2022_jp_ext • encodings.iso2022_kr • encodings.johab • encodings.shift_jis • encodings.shift_jis_2004 • encodings.shift_jisx0213

_opcode (builtin module)

imported by: opcode

_operator (builtin module)

imported by: operator

_pickle (builtin module)

imports: _compat_pickle • codecs • copyreg

imported by: pickle

_posixsubprocess (builtin module)

imports: gc

imported by: subprocess

_py_abc SourceModule

imports: _weakrefset

imported by: abc

_pydecimal SourceModule

imports: collections • contextvars • itertools • locale • math • numbers • re • sys

imported by: decimal

_queue /usr/lib/python3.11/lib-dynload/_queue.cpython-311-aarch64-linux-gnu.so

imported by: queue

_random (builtin module)

imported by: random

_sha1 (builtin module)

imported by: hashlib

_sha256 (builtin module)

imported by: hashlib

_sha3 (builtin module)

imported by: hashlib

_sha512 (builtin module)

imported by: hashlib • random

_signal (builtin module)

imported by: signal

_socket (builtin module)

imported by: socket

_sre (builtin module)

imports: copy • re

imported by: re._compiler • re._constants

_stat (builtin module)

imported by: stat

_statistics (builtin module)

imported by: statistics

_string (builtin module)

imported by: string

_strptime SourceModule

imports: _thread • calendar • datetime • locale • re • time

imported by: _datetime • datetime • time

_struct (builtin module)

imported by: struct

_thread (builtin module)

imported by: _strptime • dataclasses • functools • reprlib • tempfile • threading

_threading_local SourceModule

imports: contextlib • threading • weakref

imported by: threading

_tkinter /usr/lib/python3.11/lib-dynload/_tkinter.cpython-311-aarch64-linux-gnu.so

imported by: tkinter

_tokenize (builtin module)

imported by: tokenize

_tracemalloc (builtin module)

imported by: tracemalloc

_typing /usr/lib/python3.11/lib-dynload/_typing.cpython-311-aarch64-linux-gnu.so

imported by: typing

_warnings (builtin module)

imported by: importlib._bootstrap_external • warnings

_weakref (builtin module)

imported by: _weakrefset • collections • weakref

_weakrefset SourceModule

imports: _weakref • types

imported by: GUI_V13.py • _py_abc • threading • weakref

_winapi MissingModule

imported by: encodings • ntpath • subprocess

abc SourceModule

imports: _abc • _py_abc

imported by: GUI_V13.py • _collections_abc • contextlib • dataclasses • email._policybase • functools • importlib._abc • importlib.abc • importlib.metadata • importlib.resources.abc • inspect • io • numbers • os • selectors • typing

argparse SourceModule

imports: copy • gettext • os • re • shutil • sys • textwrap • warnings

imported by: ast • calendar • dis • gzip • inspect • py_compile • tarfile • tokenize • zipfile

array (builtin module)

imported by: serial.serialposix • serial.serialutil • socket

ast SourceModule

imports: _ast • argparse • collections • contextlib • enum • inspect • sys • warnings

imported by: inspect • traceback

atexit (builtin module)

imported by: logging • weakref

base64 SourceModule

imports: binascii • getopt • re • struct • sys

imported by: email._encoded_words • email.base64mime • email.encoders • encodings.base64_codec

binascii (builtin module)

imported by: base64 • email._encoded_words • email.base64mime • email.contentmanager • email.header • email.message • encodings.hex_codec • encodings.uu_codec • quopri • zipfile

bisect SourceModule

imports: _bisect

imported by: random • statistics

builtins (builtin module)

imported by: bz2 • codecs • dataclasses • enum • gettext • gzip • inspect • locale • lzma • operator • reprlib • subprocess • tarfile • tokenize • warnings

bz2 SourceModule

imports: _bz2 • _compression • builtins • io • os

imported by: encodings.bz2_codec • shutil • tarfile • zipfile

calendar SourceModule

imports: argparse • datetime • itertools • locale • sys

imported by: _strptime • email._parseaddr

codecs SourceModule

imports: _codecs • builtins • encodings • sys

imported by: GUI_V13.py • _pickle • encodings • encodings.ascii • encodings.base64_codec • encodings.big5 • encodings.big5hkscs • encodings.bz2_codec • encodings.charmap • encodings.cp037 • encodings.cp1006 • encodings.cp1026 • encodings.cp1125 • encodings.cp1140 • encodings.cp1250 • encodings.cp1251 • encodings.cp1252 • encodings.cp1253 • encodings.cp1254 • encodings.cp1255 • encodings.cp1256 • encodings.cp1257 • encodings.cp1258 • encodings.cp273 • encodings.cp424 • encodings.cp437 • encodings.cp500 • encodings.cp720 • encodings.cp737 • encodings.cp775 • encodings.cp850 • encodings.cp852 • encodings.cp855 • encodings.cp856 • encodings.cp857 • encodings.cp858 • encodings.cp860 • encodings.cp861 • encodings.cp862 • encodings.cp863 • encodings.cp864 • encodings.cp865 • encodings.cp866 • encodings.cp869 • encodings.cp874 • encodings.cp875 • encodings.cp932 • encodings.cp949 • encodings.cp950 • encodings.euc_jis_2004 • encodings.euc_jisx0213 • encodings.euc_jp • encodings.euc_kr • encodings.gb18030 • encodings.gb2312 • encodings.gbk • encodings.hex_codec • encodings.hp_roman8 • encodings.hz • encodings.idna • encodings.iso2022_jp • encodings.iso2022_jp_1 • encodings.iso2022_jp_2 • encodings.iso2022_jp_2004 • encodings.iso2022_jp_3 • encodings.iso2022_jp_ext • encodings.iso2022_kr • encodings.iso8859_1 • encodings.iso8859_10 • encodings.iso8859_11 • encodings.iso8859_13 • encodings.iso8859_14 • encodings.iso8859_15 • encodings.iso8859_16 • encodings.iso8859_2 • encodings.iso8859_3 • encodings.iso8859_4 • encodings.iso8859_5 • encodings.iso8859_6 • encodings.iso8859_7 • encodings.iso8859_8 • encodings.iso8859_9 • encodings.johab • encodings.koi8_r • encodings.koi8_t • encodings.koi8_u • encodings.kz1048 • encodings.latin_1 • encodings.mac_arabic • encodings.mac_croatian • encodings.mac_cyrillic • encodings.mac_farsi • encodings.mac_greek • encodings.mac_iceland • encodings.mac_latin2 • encodings.mac_roman • encodings.mac_romanian • encodings.mac_turkish • encodings.mbcs • encodings.oem • encodings.palmos • encodings.ptcp154 • encodings.punycode • encodings.quopri_codec • encodings.raw_unicode_escape • encodings.rot_13 • encodings.shift_jis • encodings.shift_jis_2004 • encodings.shift_jisx0213 • encodings.tis_620 • encodings.undefined • encodings.unicode_escape • encodings.utf_16 • encodings.utf_16_be • encodings.utf_16_le • encodings.utf_32 • encodings.utf_32_be • encodings.utf_32_le • encodings.utf_7 • encodings.utf_8 • encodings.utf_8_sig • encodings.uu_codec • encodings.zlib_codec • pickle • tokenize

collections Package

imports: _collections • _collections_abc • _weakref • copy • heapq • itertools • keyword • operator • reprlib • sys

imported by: GUI_V13.py • _pydecimal • ast • collections.abc • contextlib • dis • email.feedparser • functools • importlib.metadata • importlib.metadata._collections • importlib.resources.readers • inspect • pprint • queue • selectors • shutil • statistics • string • threading • tkinter • tokenize • typing • urllib.parse

collections.abc SourceModule

imports: _collections_abc • collections

imported by: GUI_V13.py • inspect • logging • selectors • traceback • tracemalloc • typing

contextlib SourceModule

imports: _collections_abc • abc • collections • functools • os • sys • types

imported by: _threading_local • ast • importlib.metadata • importlib.resources._adapters • importlib.resources._common • importlib.util • subprocess • traceback • typing • zipfile

contextvars SourceModule

imports: _contextvars

imported by: _pydecimal

copy SourceModule

imports: 'org.python' • copyreg • types • weakref

imported by: _sre • argparse • collections • dataclasses • email.generator • gettext • tarfile • weakref

copyreg SourceModule

imports: functools • operator

imported by: GUI_V13.py • _pickle • copy • pickle • re

csv SourceModule

imports: _csv • io • re

imported by: GUI_V13.py • importlib.metadata

ctypes Package

imports: _ctypes • ctypes._endian • nt • os • struct • sys • types

imported by: ctypes._endian • ctypes.wintypes • serial.serialwin32 • serial.win32

ctypes._endian SourceModule

imports: ctypes • sys

imported by: ctypes

ctypes.wintypes SourceModule

imports: ctypes

imported by: serial.win32

dataclasses SourceModule

imports: _thread • abc • builtins • copy • functools • inspect • itertools • keyword • re • sys • types

imported by: pprint

datetime SourceModule

imports: _datetime • _strptime • math • operator • sys • time

imported by: GUI_V13.py • _strptime • calendar • email.utils

decimal SourceModule

imports: _decimal • _pydecimal

imported by: fractions • statistics

dis SourceModule

imports: argparse • collections • io • opcode • sys • types

imported by: inspect

email Package

imports: email._header_value_parser • email.charset • email.errors • email.header • email.parser

imported by: email._encoded_words • email._header_value_parser • email._parseaddr • email._policybase • email.base64mime • email.charset • email.contentmanager • email.encoders • email.errors • email.feedparser • email.generator • email.header • email.headerregistry • email.iterators • email.message • email.parser • email.policy • email.quoprimime • email.utils • importlib.metadata

email._encoded_words SourceModule

imports: base64 • binascii • email • email.errors • functools • re • string

imported by: email._header_value_parser • email.message

email._header_value_parser SourceModule

imports: email • email._encoded_words • email.errors • email.utils • operator • re • string • sys • urllib

imported by: email • email.headerregistry

email._parseaddr SourceModule

imports: calendar • email • time

imported by: email.utils

email._policybase SourceModule

imports: abc • email • email.charset • email.header • email.utils

imported by: email.feedparser • email.message • email.parser • email.policy

email.base64mime SourceModule

imports: base64 • binascii • email

imported by: email.charset • email.header

email.charset SourceModule

imports: email • email.base64mime • email.encoders • email.errors • email.quoprimime • functools

imported by: email • email._policybase • email.contentmanager • email.header • email.message • email.utils

email.contentmanager SourceModule

imports: binascii • email • email.charset • email.errors • email.message • email.quoprimime

imported by: email.policy

email.encoders SourceModule

imports: base64 • email • quopri

imported by: email.charset

email.errors SourceModule

imports: email

imported by: email • email._encoded_words • email._header_value_parser • email.charset • email.contentmanager • email.feedparser • email.header • email.headerregistry • email.message

email.feedparser SourceModule

imports: collections • email • email._policybase • email.errors • email.message • io • re

imported by: email.parser

email.generator SourceModule

imports: copy • email • email.utils • io • random • re • sys • time

imported by: email.message

email.header SourceModule

imports: binascii • email • email.base64mime • email.charset • email.errors • email.quoprimime • re

imported by: email • email._policybase

email.headerregistry SourceModule

imports: email • email._header_value_parser • email.errors • email.utils • types

imported by: email.policy

email.iterators SourceModule

imports: email • io • sys

imported by: email.message

email.message SourceModule

imports: binascii • email • email._encoded_words • email._policybase • email.charset • email.errors • email.generator • email.iterators • email.policy • email.utils • io • quopri • re

imported by: email.contentmanager • email.feedparser • email.policy • importlib.metadata._adapters

email.parser SourceModule

imports: email • email._policybase • email.feedparser • io

imported by: email

email.policy SourceModule

imports: email • email._policybase • email.contentmanager • email.headerregistry • email.message • email.utils • re • sys

imported by: email.message

email.quoprimime SourceModule

imports: email • re • string

imported by: email.charset • email.contentmanager • email.header

email.utils SourceModule

imports: datetime • email • email._parseaddr • email.charset • os • random • re • socket • time • urllib.parse

imported by: email._header_value_parser • email._policybase • email.generator • email.headerregistry • email.message • email.policy

encodings Package

imports: _winapi • codecs • encodings • encodings.aliases • encodings.ascii • encodings.base64_codec • encodings.big5 • encodings.big5hkscs • encodings.bz2_codec • encodings.charmap • encodings.cp037 • encodings.cp1006 • encodings.cp1026 • encodings.cp1125 • encodings.cp1140 • encodings.cp1250 • encodings.cp1251 • encodings.cp1252 • encodings.cp1253 • encodings.cp1254 • encodings.cp1255 • encodings.cp1256 • encodings.cp1257 • encodings.cp1258 • encodings.cp273 • encodings.cp424 • encodings.cp437 • encodings.cp500 • encodings.cp720 • encodings.cp737 • encodings.cp775 • encodings.cp850 • encodings.cp852 • encodings.cp855 • encodings.cp856 • encodings.cp857 • encodings.cp858 • encodings.cp860 • encodings.cp861 • encodings.cp862 • encodings.cp863 • encodings.cp864 • encodings.cp865 • encodings.cp866 • encodings.cp869 • encodings.cp874 • encodings.cp875 • encodings.cp932 • encodings.cp949 • encodings.cp950 • encodings.euc_jis_2004 • encodings.euc_jisx0213 • encodings.euc_jp • encodings.euc_kr • encodings.gb18030 • encodings.gb2312 • encodings.gbk • encodings.hex_codec • encodings.hp_roman8 • encodings.hz • encodings.idna • encodings.iso2022_jp • encodings.iso2022_jp_1 • encodings.iso2022_jp_2 • encodings.iso2022_jp_2004 • encodings.iso2022_jp_3 • encodings.iso2022_jp_ext • encodings.iso2022_kr • encodings.iso8859_1 • encodings.iso8859_10 • encodings.iso8859_11 • encodings.iso8859_13 • encodings.iso8859_14 • encodings.iso8859_15 • encodings.iso8859_16 • encodings.iso8859_2 • encodings.iso8859_3 • encodings.iso8859_4 • encodings.iso8859_5 • encodings.iso8859_6 • encodings.iso8859_7 • encodings.iso8859_8 • encodings.iso8859_9 • encodings.johab • encodings.koi8_r • encodings.koi8_t • encodings.koi8_u • encodings.kz1048 • encodings.latin_1 • encodings.mac_arabic • encodings.mac_croatian • encodings.mac_cyrillic • encodings.mac_farsi • encodings.mac_greek • encodings.mac_iceland • encodings.mac_latin2 • encodings.mac_roman • encodings.mac_romanian • encodings.mac_turkish • encodings.mbcs • encodings.oem • encodings.palmos • encodings.ptcp154 • encodings.punycode • encodings.quopri_codec • encodings.raw_unicode_escape • encodings.rot_13 • encodings.shift_jis • encodings.shift_jis_2004 • encodings.shift_jisx0213 • encodings.tis_620 • encodings.undefined • encodings.unicode_escape • encodings.utf_16 • encodings.utf_16_be • encodings.utf_16_le • encodings.utf_32 • encodings.utf_32_be • encodings.utf_32_le • encodings.utf_7 • encodings.utf_8 • encodings.utf_8_sig • encodings.uu_codec • encodings.zlib_codec • sys

imported by: GUI_V13.py • codecs • encodings • encodings.aliases • encodings.ascii • encodings.base64_codec • encodings.big5 • encodings.big5hkscs • encodings.bz2_codec • encodings.charmap • encodings.cp037 • encodings.cp1006 • encodings.cp1026 • encodings.cp1125 • encodings.cp1140 • encodings.cp1250 • encodings.cp1251 • encodings.cp1252 • encodings.cp1253 • encodings.cp1254 • encodings.cp1255 • encodings.cp1256 • encodings.cp1257 • encodings.cp1258 • encodings.cp273 • encodings.cp424 • encodings.cp437 • encodings.cp500 • encodings.cp720 • encodings.cp737 • encodings.cp775 • encodings.cp850 • encodings.cp852 • encodings.cp855 • encodings.cp856 • encodings.cp857 • encodings.cp858 • encodings.cp860 • encodings.cp861 • encodings.cp862 • encodings.cp863 • encodings.cp864 • encodings.cp865 • encodings.cp866 • encodings.cp869 • encodings.cp874 • encodings.cp875 • encodings.cp932 • encodings.cp949 • encodings.cp950 • encodings.euc_jis_2004 • encodings.euc_jisx0213 • encodings.euc_jp • encodings.euc_kr • encodings.gb18030 • encodings.gb2312 • encodings.gbk • encodings.hex_codec • encodings.hp_roman8 • encodings.hz • encodings.idna • encodings.iso2022_jp • encodings.iso2022_jp_1 • encodings.iso2022_jp_2 • encodings.iso2022_jp_2004 • encodings.iso2022_jp_3 • encodings.iso2022_jp_ext • encodings.iso2022_kr • encodings.iso8859_1 • encodings.iso8859_10 • encodings.iso8859_11 • encodings.iso8859_13 • encodings.iso8859_14 • encodings.iso8859_15 • encodings.iso8859_16 • encodings.iso8859_2 • encodings.iso8859_3 • encodings.iso8859_4 • encodings.iso8859_5 • encodings.iso8859_6 • encodings.iso8859_7 • encodings.iso8859_8 • encodings.iso8859_9 • encodings.johab • encodings.koi8_r • encodings.koi8_t • encodings.koi8_u • encodings.kz1048 • encodings.latin_1 • encodings.mac_arabic • encodings.mac_croatian • encodings.mac_cyrillic • encodings.mac_farsi • encodings.mac_greek • encodings.mac_iceland • encodings.mac_latin2 • encodings.mac_roman • encodings.mac_romanian • encodings.mac_turkish • encodings.mbcs • encodings.oem • encodings.palmos • encodings.ptcp154 • encodings.punycode • encodings.quopri_codec • encodings.raw_unicode_escape • encodings.rot_13 • encodings.shift_jis • encodings.shift_jis_2004 • encodings.shift_jisx0213 • encodings.tis_620 • encodings.undefined • encodings.unicode_escape • encodings.utf_16 • encodings.utf_16_be • encodings.utf_16_le • encodings.utf_32 • encodings.utf_32_be • encodings.utf_32_le • encodings.utf_7 • encodings.utf_8 • encodings.utf_8_sig • encodings.uu_codec • encodings.zlib_codec • locale

encodings.aliases SourceModule

imports: encodings

imported by: GUI_V13.py • encodings • locale

encodings.ascii SourceModule

imports: codecs • encodings

imported by: GUI_V13.py • encodings

encodings.base64_codec SourceModule

imports: base64 • codecs • encodings

imported by: GUI_V13.py • encodings

encodings.big5 SourceModule

imports: _codecs_tw • _multibytecodec • codecs • encodings

imported by: GUI_V13.py • encodings

encodings.big5hkscs SourceModule

imports: _codecs_hk • _multibytecodec • codecs • encodings

imported by: GUI_V13.py • encodings

encodings.bz2_codec SourceModule

imports: bz2 • codecs • encodings

imported by: GUI_V13.py • encodings

encodings.charmap SourceModule

imports: codecs • encodings

imported by: GUI_V13.py • encodings

encodings.cp037 SourceModule

imports: codecs • encodings

imported by: GUI_V13.py • encodings

encodings.cp1006 SourceModule

imports: codecs • encodings

imported by: GUI_V13.py • encodings

encodings.cp1026 SourceModule

imports: codecs • encodings

imported by: GUI_V13.py • encodings

encodings.cp1125 SourceModule

imports: codecs • encodings

imported by: GUI_V13.py • encodings

encodings.cp1140 SourceModule

imports: codecs • encodings

imported by: GUI_V13.py • encodings

encodings.cp1250 SourceModule

imports: codecs • encodings

imported by: GUI_V13.py • encodings

encodings.cp1251 SourceModule

imports: codecs • encodings

imported by: GUI_V13.py • encodings

encodings.cp1252 SourceModule

imports: codecs • encodings

imported by: GUI_V13.py • encodings

encodings.cp1253 SourceModule

imports: codecs • encodings

imported by: GUI_V13.py • encodings

encodings.cp1254 SourceModule

imports: codecs • encodings

imported by: GUI_V13.py • encodings

encodings.cp1255 SourceModule

imports: codecs • encodings

imported by: GUI_V13.py • encodings

encodings.cp1256 SourceModule

imports: codecs • encodings

imported by: GUI_V13.py • encodings

encodings.cp1257 SourceModule

imports: codecs • encodings

imported by: GUI_V13.py • encodings

encodings.cp1258 SourceModule

imports: codecs • encodings

imported by: GUI_V13.py • encodings

encodings.cp273 SourceModule

imports: codecs • encodings

imported by: GUI_V13.py • encodings

encodings.cp424 SourceModule

imports: codecs • encodings

imported by: GUI_V13.py • encodings

encodings.cp437 SourceModule

imports: codecs • encodings

imported by: GUI_V13.py • encodings

encodings.cp500 SourceModule

imports: codecs • encodings

imported by: GUI_V13.py • encodings

encodings.cp720 SourceModule

imports: codecs • encodings

imported by: GUI_V13.py • encodings

encodings.cp737 SourceModule

imports: codecs • encodings

imported by: GUI_V13.py • encodings

encodings.cp775 SourceModule

imports: codecs • encodings

imported by: GUI_V13.py • encodings

encodings.cp850 SourceModule

imports: codecs • encodings

imported by: GUI_V13.py • encodings

encodings.cp852 SourceModule

imports: codecs • encodings

imported by: GUI_V13.py • encodings

encodings.cp855 SourceModule

imports: codecs • encodings

imported by: GUI_V13.py • encodings

encodings.cp856 SourceModule

imports: codecs • encodings

imported by: GUI_V13.py • encodings

encodings.cp857 SourceModule

imports: codecs • encodings

imported by: GUI_V13.py • encodings

encodings.cp858 SourceModule

imports: codecs • encodings

imported by: GUI_V13.py • encodings

encodings.cp860 SourceModule

imports: codecs • encodings

imported by: GUI_V13.py • encodings

encodings.cp861 SourceModule

imports: codecs • encodings

imported by: GUI_V13.py • encodings

encodings.cp862 SourceModule

imports: codecs • encodings

imported by: GUI_V13.py • encodings

encodings.cp863 SourceModule

imports: codecs • encodings

imported by: GUI_V13.py • encodings

encodings.cp864 SourceModule

imports: codecs • encodings

imported by: GUI_V13.py • encodings

encodings.cp865 SourceModule

imports: codecs • encodings

imported by: GUI_V13.py • encodings

encodings.cp866 SourceModule

imports: codecs • encodings

imported by: GUI_V13.py • encodings

encodings.cp869 SourceModule

imports: codecs • encodings

imported by: GUI_V13.py • encodings

encodings.cp874 SourceModule

imports: codecs • encodings

imported by: GUI_V13.py • encodings

encodings.cp875 SourceModule

imports: codecs • encodings

imported by: GUI_V13.py • encodings

encodings.cp932 SourceModule

imports: _codecs_jp • _multibytecodec • codecs • encodings

imported by: GUI_V13.py • encodings

encodings.cp949 SourceModule

imports: _codecs_kr • _multibytecodec • codecs • encodings

imported by: GUI_V13.py • encodings

encodings.cp950 SourceModule

imports: _codecs_tw • _multibytecodec • codecs • encodings

imported by: GUI_V13.py • encodings

encodings.euc_jis_2004 SourceModule

imports: _codecs_jp • _multibytecodec • codecs • encodings

imported by: GUI_V13.py • encodings

encodings.euc_jisx0213 SourceModule

imports: _codecs_jp • _multibytecodec • codecs • encodings

imported by: GUI_V13.py • encodings

encodings.euc_jp SourceModule

imports: _codecs_jp • _multibytecodec • codecs • encodings

imported by: GUI_V13.py • encodings

encodings.euc_kr SourceModule

imports: _codecs_kr • _multibytecodec • codecs • encodings

imported by: GUI_V13.py • encodings

encodings.gb18030 SourceModule

imports: _codecs_cn • _multibytecodec • codecs • encodings

imported by: GUI_V13.py • encodings

encodings.gb2312 SourceModule

imports: _codecs_cn • _multibytecodec • codecs • encodings

imported by: GUI_V13.py • encodings

encodings.gbk SourceModule

imports: _codecs_cn • _multibytecodec • codecs • encodings

imported by: GUI_V13.py • encodings

encodings.hex_codec SourceModule

imports: binascii • codecs • encodings

imported by: GUI_V13.py • encodings

encodings.hp_roman8 SourceModule

imports: codecs • encodings

imported by: GUI_V13.py • encodings

encodings.hz SourceModule

imports: _codecs_cn • _multibytecodec • codecs • encodings

imported by: GUI_V13.py • encodings

encodings.idna SourceModule

imports: codecs • encodings • re • stringprep • unicodedata

imported by: GUI_V13.py • encodings

encodings.iso2022_jp SourceModule

imports: _codecs_iso2022 • _multibytecodec • codecs • encodings

imported by: GUI_V13.py • encodings

encodings.iso2022_jp_1 SourceModule

imports: _codecs_iso2022 • _multibytecodec • codecs • encodings

imported by: GUI_V13.py • encodings

encodings.iso2022_jp_2 SourceModule

imports: _codecs_iso2022 • _multibytecodec • codecs • encodings

imported by: GUI_V13.py • encodings

encodings.iso2022_jp_2004 SourceModule

imports: _codecs_iso2022 • _multibytecodec • codecs • encodings

imported by: GUI_V13.py • encodings

encodings.iso2022_jp_3 SourceModule

imports: _codecs_iso2022 • _multibytecodec • codecs • encodings

imported by: GUI_V13.py • encodings

encodings.iso2022_jp_ext SourceModule

imports: _codecs_iso2022 • _multibytecodec • codecs • encodings

imported by: GUI_V13.py • encodings

encodings.iso2022_kr SourceModule

imports: _codecs_iso2022 • _multibytecodec • codecs • encodings

imported by: GUI_V13.py • encodings

encodings.iso8859_1 SourceModule

imports: codecs • encodings

imported by: GUI_V13.py • encodings

encodings.iso8859_10 SourceModule

imports: codecs • encodings

imported by: GUI_V13.py • encodings

encodings.iso8859_11 SourceModule

imports: codecs • encodings

imported by: GUI_V13.py • encodings

encodings.iso8859_13 SourceModule

imports: codecs • encodings

imported by: GUI_V13.py • encodings

encodings.iso8859_14 SourceModule

imports: codecs • encodings

imported by: GUI_V13.py • encodings

encodings.iso8859_15 SourceModule

imports: codecs • encodings

imported by: GUI_V13.py • encodings

encodings.iso8859_16 SourceModule

imports: codecs • encodings

imported by: GUI_V13.py • encodings

encodings.iso8859_2 SourceModule

imports: codecs • encodings

imported by: GUI_V13.py • encodings

encodings.iso8859_3 SourceModule

imports: codecs • encodings

imported by: GUI_V13.py • encodings

encodings.iso8859_4 SourceModule

imports: codecs • encodings

imported by: GUI_V13.py • encodings

encodings.iso8859_5 SourceModule

imports: codecs • encodings

imported by: GUI_V13.py • encodings

encodings.iso8859_6 SourceModule

imports: codecs • encodings

imported by: GUI_V13.py • encodings

encodings.iso8859_7 SourceModule

imports: codecs • encodings

imported by: GUI_V13.py • encodings

encodings.iso8859_8 SourceModule

imports: codecs • encodings

imported by: GUI_V13.py • encodings

encodings.iso8859_9 SourceModule

imports: codecs • encodings

imported by: GUI_V13.py • encodings

encodings.johab SourceModule

imports: _codecs_kr • _multibytecodec • codecs • encodings

imported by: GUI_V13.py • encodings

encodings.koi8_r SourceModule

imports: codecs • encodings

imported by: GUI_V13.py • encodings

encodings.koi8_t SourceModule

imports: codecs • encodings

imported by: GUI_V13.py • encodings

encodings.koi8_u SourceModule

imports: codecs • encodings

imported by: GUI_V13.py • encodings

encodings.kz1048 SourceModule

imports: codecs • encodings

imported by: GUI_V13.py • encodings

encodings.latin_1 SourceModule

imports: codecs • encodings

imported by: GUI_V13.py • encodings

encodings.mac_arabic SourceModule

imports: codecs • encodings

imported by: GUI_V13.py • encodings

encodings.mac_croatian SourceModule

imports: codecs • encodings

imported by: GUI_V13.py • encodings

encodings.mac_cyrillic SourceModule

imports: codecs • encodings

imported by: GUI_V13.py • encodings

encodings.mac_farsi SourceModule

imports: codecs • encodings

imported by: GUI_V13.py • encodings

encodings.mac_greek SourceModule

imports: codecs • encodings

imported by: GUI_V13.py • encodings

encodings.mac_iceland SourceModule

imports: codecs • encodings

imported by: GUI_V13.py • encodings

encodings.mac_latin2 SourceModule

imports: codecs • encodings

imported by: GUI_V13.py • encodings

encodings.mac_roman SourceModule

imports: codecs • encodings

imported by: GUI_V13.py • encodings

encodings.mac_romanian SourceModule

imports: codecs • encodings

imported by: GUI_V13.py • encodings

encodings.mac_turkish SourceModule

imports: codecs • encodings

imported by: GUI_V13.py • encodings

encodings.mbcs SourceModule

imports: codecs • encodings

imported by: GUI_V13.py • encodings

encodings.oem SourceModule

imports: codecs • encodings

imported by: GUI_V13.py • encodings

encodings.palmos SourceModule

imports: codecs • encodings

imported by: GUI_V13.py • encodings

encodings.ptcp154 SourceModule

imports: codecs • encodings

imported by: GUI_V13.py • encodings

encodings.punycode SourceModule

imports: codecs • encodings

imported by: GUI_V13.py • encodings

encodings.quopri_codec SourceModule

imports: codecs • encodings • io • quopri

imported by: GUI_V13.py • encodings

encodings.raw_unicode_escape SourceModule

imports: codecs • encodings

imported by: GUI_V13.py • encodings

encodings.rot_13 SourceModule

imports: codecs • encodings • sys

imported by: GUI_V13.py • encodings

encodings.shift_jis SourceModule

imports: _codecs_jp • _multibytecodec • codecs • encodings

imported by: GUI_V13.py • encodings

encodings.shift_jis_2004 SourceModule

imports: _codecs_jp • _multibytecodec • codecs • encodings

imported by: GUI_V13.py • encodings

encodings.shift_jisx0213 SourceModule

imports: _codecs_jp • _multibytecodec • codecs • encodings

imported by: GUI_V13.py • encodings

encodings.tis_620 SourceModule

imports: codecs • encodings

imported by: GUI_V13.py • encodings

encodings.undefined SourceModule

imports: codecs • encodings

imported by: GUI_V13.py • encodings

encodings.unicode_escape SourceModule

imports: codecs • encodings

imported by: GUI_V13.py • encodings

encodings.utf_16 SourceModule

imports: codecs • encodings • sys

imported by: GUI_V13.py • encodings

encodings.utf_16_be SourceModule

imports: codecs • encodings

imported by: GUI_V13.py • encodings

encodings.utf_16_le SourceModule

imports: codecs • encodings

imported by: GUI_V13.py • encodings

encodings.utf_32 SourceModule

imports: codecs • encodings • sys

imported by: GUI_V13.py • encodings

encodings.utf_32_be SourceModule

imports: codecs • encodings

imported by: GUI_V13.py • encodings

encodings.utf_32_le SourceModule

imports: codecs • encodings

imported by: GUI_V13.py • encodings

encodings.utf_7 SourceModule

imports: codecs • encodings

imported by: GUI_V13.py • encodings

encodings.utf_8 SourceModule

imports: codecs • encodings

imported by: GUI_V13.py • encodings

encodings.utf_8_sig SourceModule

imports: codecs • encodings

imported by: GUI_V13.py • encodings

encodings.uu_codec SourceModule

imports: binascii • codecs • encodings • io

imported by: GUI_V13.py • encodings

encodings.zlib_codec SourceModule

imports: codecs • encodings • zlib

imported by: GUI_V13.py • encodings

enum SourceModule

imports: builtins • functools • operator • sys • types • warnings

imported by: GUI_V13.py • ast • inspect • py_compile • re • signal • socket • tkinter

errno (builtin module)

imported by: gettext • gzip • pathlib • serial.serialposix • shutil • socket • subprocess • tempfile

fcntl (builtin module)

imported by: serial.serialposix • subprocess

fnmatch SourceModule

imports: functools • os • posixpath • re

imported by: pathlib • shutil • tkinter.filedialog • tracemalloc

fractions SourceModule

imports: decimal • math • numbers • operator • re • sys

imported by: statistics

functools SourceModule

imports: _functools • _thread • abc • collections • reprlib • types • typing • weakref

imported by: GUI_V13.py • contextlib • copyreg • dataclasses • email._encoded_words • email.charset • enum • fnmatch • importlib.metadata • importlib.metadata._functools • importlib.resources._common • importlib.resources._legacy • importlib.util • inspect • linecache • locale • operator • pathlib • pickle • re • statistics • tempfile • threading • tokenize • tracemalloc • types • typing • urllib.parse

gc (builtin module)

imports: time

imported by: _posixsubprocess • weakref

genericpath SourceModule

imports: os • stat

imported by: GUI_V13.py • ntpath • posixpath

getopt SourceModule

imports: gettext • os • sys

imported by: base64 • quopri

gettext SourceModule

imports: builtins • copy • errno • locale • os • re • struct • sys • warnings

imported by: argparse • getopt

grp (builtin module)

imported by: pathlib • shutil • subprocess • tarfile

gzip SourceModule

imports: _compression • argparse • builtins • errno • io • os • struct • sys • time • warnings • zlib

imported by: tarfile

hashlib SourceModule

imports: _blake2 • _hashlib • _md5 • _sha1 • _sha256 • _sha3 • _sha512 • logging • warnings

imported by: random

heapq SourceModule

imports: _heapq

imported by: GUI_V13.py • collections • queue

importlib Package

imports: _frozen_importlib • _frozen_importlib_external • _imp • importlib • importlib._bootstrap • importlib._bootstrap_external • sys • warnings

imported by: importlib • importlib._abc • importlib._bootstrap • importlib._bootstrap_external • importlib.abc • importlib.machinery • importlib.metadata • importlib.readers • importlib.resources • importlib.resources._common • importlib.util • inspect • serial

importlib._abc SourceModule

imports: abc • importlib • importlib._bootstrap • warnings

imported by: importlib.abc • importlib.util

importlib._bootstrap SourceModule

imports: _frozen_importlib_external • importlib

imported by: importlib • importlib._abc • importlib.machinery • importlib.util

importlib._bootstrap_external SourceModule

imports: _imp • _io • _warnings • importlib • importlib.metadata • importlib.readers • marshal • nt • posix • sys • tokenize • winreg

imported by: importlib • importlib.abc • importlib.machinery • importlib.util • py_compile

importlib.abc SourceModule

imports: _frozen_importlib • _frozen_importlib_external • abc • importlib • importlib._abc • importlib._bootstrap_external • importlib.machinery • importlib.resources.abc • warnings

imported by: importlib.metadata

importlib.machinery SourceModule

imports: importlib • importlib._bootstrap • importlib._bootstrap_external

imported by: importlib.abc • inspect • py_compile

importlib.metadata Package

imports: abc • collections • contextlib • csv • email • functools • importlib • importlib.abc • importlib.metadata • importlib.metadata._adapters • importlib.metadata._collections • importlib.metadata._functools • importlib.metadata._itertools • importlib.metadata._meta • itertools • operator • os • pathlib • posixpath • re • sys • textwrap • typing • warnings • zipfile

imported by: importlib._bootstrap_external • importlib.metadata • importlib.metadata._adapters • importlib.metadata._collections • importlib.metadata._functools • importlib.metadata._itertools • importlib.metadata._meta • importlib.metadata._text

importlib.metadata._adapters SourceModule

imports: email.message • importlib.metadata • importlib.metadata._text • re • textwrap

imported by: importlib.metadata

importlib.metadata._collections SourceModule

imports: collections • importlib.metadata

imported by: importlib.metadata

importlib.metadata._functools SourceModule

imports: functools • importlib.metadata • types

imported by: importlib.metadata • importlib.metadata._text

importlib.metadata._itertools SourceModule

imports: importlib.metadata • itertools

imported by: importlib.metadata

importlib.metadata._meta SourceModule

imports: importlib.metadata • typing

imported by: importlib.metadata

importlib.metadata._text SourceModule

imports: importlib.metadata • importlib.metadata._functools • re

imported by: importlib.metadata._adapters

importlib.readers SourceModule

imports: importlib • importlib.resources.readers

imported by: importlib._bootstrap_external

importlib.resources Package

imports: importlib • importlib.resources • importlib.resources._common • importlib.resources._legacy • importlib.resources.abc

imported by: importlib.resources • importlib.resources._adapters • importlib.resources._common • importlib.resources._itertools • importlib.resources._legacy • importlib.resources.abc • importlib.resources.readers

importlib.resources._adapters SourceModule

imports: contextlib • importlib.resources • importlib.resources.abc • io

imported by: importlib.resources._common

importlib.resources._common SourceModule

imports: contextlib • functools • importlib • importlib.resources • importlib.resources._adapters • importlib.resources.abc • os • pathlib • tempfile • types • typing

imported by: importlib.resources • importlib.resources._legacy

importlib.resources._itertools SourceModule

imports: importlib.resources • itertools • typing

imported by: importlib.resources.readers

importlib.resources._legacy SourceModule

imports: functools • importlib.resources • importlib.resources._common • os • pathlib • types • typing • warnings

imported by: importlib.resources

importlib.resources.abc SourceModule

imports: abc • importlib.resources • io • os • typing

imported by: importlib.abc • importlib.resources • importlib.resources._adapters • importlib.resources._common • importlib.resources.readers

importlib.resources.readers SourceModule

imports: collections • importlib.resources • importlib.resources._itertools • importlib.resources.abc • operator • pathlib • zipfile

imported by: importlib.readers

importlib.util SourceModule

imports: _imp • contextlib • functools • importlib • importlib._abc • importlib._bootstrap • importlib._bootstrap_external • sys • types • warnings

imported by: py_compile • zipfile

inspect SourceModule

imports: abc • argparse • ast • builtins • collections • collections.abc • dis • enum • functools • importlib • importlib.machinery • itertools • keyword • linecache • operator • os • re • sys • token • tokenize • types

imported by: ast • dataclasses • pyi_rth_inspect.py

io SourceModule

imports: _io • abc • warnings

imported by: GUI_V13.py • _compression • bz2 • csv • dis • email.feedparser • email.generator • email.iterators • email.message • email.parser • encodings.quopri_codec • encodings.uu_codec • gzip • importlib.resources._adapters • importlib.resources.abc • logging • lzma • os • pathlib • pickle • pprint • quopri • serial.serialutil • socket • subprocess • tarfile • tempfile • tokenize • zipfile

itertools (builtin module)

imported by: _pydecimal • calendar • collections • dataclasses • importlib.metadata • importlib.metadata._itertools • importlib.resources._itertools • inspect • pickle • random • reprlib • statistics • threading • tkinter.font • tokenize • traceback • weakref • zipfile

keyword SourceModule

imported by: GUI_V13.py • collections • dataclasses • inspect

linecache SourceModule

imports: functools • os • sys • tokenize

imported by: GUI_V13.py • inspect • traceback • tracemalloc • warnings

locale SourceModule

imports: _collections_abc • _locale • builtins • encodings • encodings.aliases • functools • os • re • sys • warnings

imported by: GUI_V13.py • _pydecimal • _strptime • calendar • gettext • subprocess • tkinter.filedialog

logging Package

imports: atexit • collections.abc • io • os • pickle • re • string • sys • threading • time • traceback • types • warnings • weakref

imported by: GUI_V13.py • hashlib

lzma SourceModule

imports: _compression • _lzma • builtins • io • os

imported by: shutil • tarfile • zipfile

marshal (builtin module)

imported by: importlib._bootstrap_external

math (builtin module)

imported by: _pydecimal • datetime • fractions • random • selectors • statistics

msvcrt MissingModule

imported by: subprocess

nt MissingModule

imported by: ctypes • importlib._bootstrap_external • ntpath • os • shutil

ntpath SourceModule

imports: _winapi • genericpath • nt • os • stat • string • sys

imported by: GUI_V13.py • os • pathlib

numbers SourceModule

imports: abc

imported by: _pydecimal • fractions • statistics

opcode SourceModule

imports: _opcode

imported by: dis

operator SourceModule

imports: _operator • builtins • functools

imported by: GUI_V13.py • collections • copyreg • datetime • email._header_value_parser • enum • fractions • importlib.metadata • importlib.resources.readers • inspect • pathlib • random • statistics • typing

org MissingModule

imported by: pickle

os SourceModule

imports: _collections_abc • abc • io • nt • ntpath • os.path • posix • posixpath • stat • subprocess • sys • warnings

imported by: GUI_V13.py • argparse • bz2 • contextlib • ctypes • email.utils • fnmatch • genericpath • getopt • gettext • gzip • importlib.metadata • importlib.resources._common • importlib.resources._legacy • importlib.resources.abc • inspect • linecache • locale • logging • lzma • ntpath • os.path • pathlib • posixpath • py_compile • pyi_rth__tkinter.py • pyi_rth_inspect.py • random • serial • serial.serialposix • shutil • socket • subprocess • tarfile • tempfile • threading • tkinter • tkinter.filedialog • zipfile

os.path AliasNode

imports: os • posixpath

imported by: os • py_compile • tracemalloc

pathlib SourceModule

imports: _collections_abc • errno • fnmatch • functools • grp • io • ntpath • operator • os • posixpath • pwd • re • stat • sys • urllib.parse • warnings

imported by: importlib.metadata • importlib.resources._common • importlib.resources._legacy • importlib.resources.readers • zipfile

pickle SourceModule

imports: _compat_pickle • _pickle • codecs • copyreg • functools • io • itertools • org • pprint • re • struct • sys • types

imported by: logging • tracemalloc

posix (builtin module)

imports: resource

imported by: importlib._bootstrap_external • os • posixpath • shutil

posixpath SourceModule

imports: genericpath • os • posix • pwd • re • stat • sys

imported by: GUI_V13.py • fnmatch • importlib.metadata • os • os.path • pathlib • zipfile

pprint SourceModule

imports: collections • dataclasses • io • re • sys • time • types

imported by: pickle

pwd (builtin module)

imported by: pathlib • posixpath • shutil • subprocess • tarfile

py_compile SourceModule

imports: argparse • enum • importlib._bootstrap_external • importlib.machinery • importlib.util • os • os.path • sys • traceback

imported by: zipfile

queue SourceModule

imports: _queue • collections • heapq • threading • time • types

imported by: GUI_V13.py

quopri SourceModule

imports: binascii • getopt • io • sys

imported by: email.encoders • email.message • encodings.quopri_codec

random SourceModule

imports: _collections_abc • _random • _sha512 • bisect • hashlib • itertools • math • operator • os • statistics • time • warnings

imported by: email.generator • email.utils • statistics • tempfile

re Package

imports: copyreg • enum • functools • re • re._compiler • re._constants • re._parser • warnings

imported by: GUI_V13.py • _pydecimal • _sre • _strptime • argparse • base64 • csv • dataclasses • email._encoded_words • email._header_value_parser • email.feedparser • email.generator • email.header • email.message • email.policy • email.quoprimime • email.utils • encodings.idna • fnmatch • fractions • gettext • importlib.metadata • importlib.metadata._adapters • importlib.metadata._text • inspect • locale • logging • pathlib • pickle • posixpath • pprint • re • re._casefix • re._compiler • re._constants • re._parser • sre_compile • sre_constants • sre_parse • string • tarfile • textwrap • tkinter • tokenize • typing • urllib.parse • warnings • zipfile

re._casefix SourceModule

imports: re

imported by: GUI_V13.py • re._compiler

re._compiler SourceModule

imports: _sre • re • re._casefix • re._constants • re._parser • sys

imported by: GUI_V13.py • re • sre_compile

re._constants SourceModule

imports: _sre • re

imported by: GUI_V13.py • re • re._compiler • re._parser • sre_constants

re._parser SourceModule

imports: re • re._constants • unicodedata • warnings

imported by: GUI_V13.py • re • re._compiler • sre_parse

reprlib SourceModule

imports: _thread • builtins • itertools

imported by: GUI_V13.py • collections • functools

resource /usr/lib/python3.11/lib-dynload/resource.cpython-311-aarch64-linux-gnu.so

imported by: posix

select (builtin module)

imported by: selectors • serial.serialposix • subprocess

selectors SourceModule

imports: abc • collections • collections.abc • math • select • sys

imported by: socket • subprocess

serial Package

imports: __future__ • importlib • os • serial.serialcli • serial.serialjava • serial.serialposix • serial.serialutil • serial.serialwin32 • serial.win32 • sys

imported by: GUI_V13.py • serial.serialcli • serial.serialjava • serial.serialposix • serial.serialutil • serial.serialwin32 • serial.win32

serial.serialcli SourceModule

imports: 'System.IO' • System • __future__ • serial • serial.serialutil

imported by: serial

serial.serialjava SourceModule

imports: __future__ • serial • serial.serialutil

imported by: serial

serial.serialposix SourceModule

imports: __future__ • array • errno • fcntl • os • select • serial • serial.serialutil • struct • sys • termios • warnings

imported by: serial

serial.serialutil SourceModule

imports: __future__ • array • io • serial • sys • time

imported by: serial • serial.serialcli • serial.serialjava • serial.serialposix • serial.serialwin32

serial.serialwin32 SourceModule

imports: __future__ • ctypes • serial • serial.serialutil • serial.win32 • time

imported by: serial

serial.win32 SourceModule

imports: __future__ • ctypes • ctypes.wintypes • serial

imported by: serial • serial.serialwin32

shutil SourceModule

imports: bz2 • collections • errno • fnmatch • grp • lzma • nt • os • posix • pwd • stat • sys • tarfile • zipfile • zlib

imported by: argparse • tarfile • tempfile • zipfile

signal SourceModule

imports: _signal • enum

imported by: subprocess

socket SourceModule

imports: _socket • array • enum • errno • io • os • selectors • sys

imported by: email.utils

sre_compile SourceModule

imports: re • re._compiler • warnings

imported by: GUI_V13.py

sre_constants SourceModule

imports: re • re._constants • warnings

imported by: GUI_V13.py

sre_parse SourceModule

imports: re • re._parser • warnings

imported by: GUI_V13.py

stat SourceModule

imports: _stat

imported by: GUI_V13.py • genericpath • ntpath • os • pathlib • posixpath • shutil • tarfile • tempfile • zipfile

statistics SourceModule

imports: _statistics • bisect • collections • decimal • fractions • functools • itertools • math • numbers • operator • random • sys

imported by: random

string SourceModule

imports: _string • collections • re

imported by: email._encoded_words • email._header_value_parser • email.quoprimime • logging • ntpath

stringprep SourceModule

imports: unicodedata

imported by: encodings.idna

struct SourceModule

imports: _struct

imported by: base64 • ctypes • gettext • gzip • pickle • serial.serialposix • tarfile • zipfile

subprocess SourceModule

imports: _posixsubprocess • _winapi • builtins • contextlib • errno • fcntl • grp • io • locale • msvcrt • os • pwd • select • selectors • signal • sys • threading • time • types • warnings

imported by: os

sys (builtin module)

imported by: GUI_V13.py • _collections_abc • _compression • _pydecimal • argparse • ast • base64 • calendar • codecs • collections • contextlib • ctypes • ctypes._endian • dataclasses • datetime • dis • email._header_value_parser • email.generator • email.iterators • email.policy • encodings • encodings.rot_13 • encodings.utf_16 • encodings.utf_32 • enum • fractions • getopt • gettext • gzip • importlib • importlib._bootstrap_external • importlib.metadata • importlib.util • inspect • linecache • locale • logging • ntpath • os • pathlib • pickle • posixpath • pprint • py_compile • pyi_rth__tkinter.py • pyi_rth_inspect.py • quopri • re._compiler • selectors • serial • serial.serialposix • serial.serialutil • shutil • socket • statistics • subprocess • tarfile • tempfile • threading • tkinter • tkinter.filedialog • tokenize • traceback • types • typing • urllib.parse • warnings • weakref • zipfile

tarfile SourceModule

imports: argparse • builtins • bz2 • copy • grp • gzip • io • lzma • os • pwd • re • shutil • stat • struct • sys • time • zlib

imported by: shutil

tempfile SourceModule

imports: _thread • errno • functools • io • os • random • shutil • stat • sys • types • warnings • weakref

imported by: importlib.resources._common

termios /usr/lib/python3.11/lib-dynload/termios.cpython-311-aarch64-linux-gnu.so

imported by: serial.serialposix

textwrap SourceModule

imports: re

imported by: argparse • importlib.metadata • importlib.metadata._adapters • traceback

threading SourceModule

imports: _collections • _thread • _threading_local • _weakrefset • collections • functools • itertools • os • sys • time • traceback • warnings

imported by: GUI_V13.py • _threading_local • logging • queue • subprocess • zipfile

time (builtin module)

imports: _strptime

imported by: GUI_V13.py • _datetime • _strptime • datetime • email._parseaddr • email.generator • email.utils • gc • gzip • logging • pprint • queue • random • serial.serialutil • serial.serialwin32 • subprocess • tarfile • threading • zipfile

tkinter Package

imports: _tkinter • collections • enum • os • re • sys • tkinter.commondialog • tkinter.constants • tkinter.filedialog • tkinter.font • tkinter.messagebox • tkinter.ttk • traceback • types

imported by: GUI_V13.py • tkinter.commondialog • tkinter.constants • tkinter.dialog • tkinter.filedialog • tkinter.font • tkinter.messagebox • tkinter.simpledialog • tkinter.ttk

tkinter.commondialog SourceModule

imports: tkinter

imported by: tkinter • tkinter.filedialog • tkinter.messagebox

tkinter.constants SourceModule

imports: tkinter

imported by: tkinter

tkinter.dialog SourceModule

imports: tkinter

imported by: tkinter.filedialog

tkinter.filedialog SourceModule

imports: fnmatch • locale • os • sys • tkinter • tkinter.commondialog • tkinter.dialog • tkinter.simpledialog

imported by: GUI_V13.py • tkinter

tkinter.font SourceModule

imports: itertools • tkinter

imported by: GUI_V13.py • tkinter

tkinter.messagebox SourceModule

imports: tkinter • tkinter.commondialog

imported by: tkinter • tkinter.simpledialog

tkinter.simpledialog SourceModule

imports: tkinter • tkinter.messagebox

imported by: tkinter.filedialog

tkinter.ttk SourceModule

imports: tkinter

imported by: GUI_V13.py • tkinter

token SourceModule

imported by: inspect • tokenize

tokenize SourceModule

imports: _tokenize • argparse • builtins • codecs • collections • functools • io • itertools • re • sys • token

imported by: importlib._bootstrap_external • inspect • linecache

traceback SourceModule

imports: ast • collections.abc • contextlib • itertools • linecache • sys • textwrap

imported by: GUI_V13.py • logging • py_compile • threading • tkinter • warnings

tracemalloc SourceModule

imports: _tracemalloc • collections.abc • fnmatch • functools • linecache • os.path • pickle

imported by: warnings

types SourceModule

imports: _collections_abc • functools • sys

imported by: GUI_V13.py • _weakrefset • contextlib • copy • ctypes • dataclasses • dis • email.headerregistry • enum • functools • importlib.metadata._functools • importlib.resources._common • importlib.resources._legacy • importlib.util • inspect • logging • pickle • pprint • queue • subprocess • tempfile • tkinter • typing • urllib.parse

typing SourceModule

imports: _typing • abc • collections • collections.abc • contextlib • functools • operator • re • sys • types • warnings

imported by: functools • importlib.metadata • importlib.metadata._meta • importlib.resources._common • importlib.resources._itertools • importlib.resources._legacy • importlib.resources.abc

unicodedata (builtin module)

imported by: encodings.idna • re._parser • stringprep • urllib.parse

urllib Package

imported by: email._header_value_parser • urllib.parse

urllib.parse SourceModule

imports: collections • functools • re • sys • types • unicodedata • urllib • warnings

imported by: email.utils • pathlib

warnings SourceModule

imports: _warnings • builtins • linecache • re • sys • traceback • tracemalloc

imported by: GUI_V13.py • argparse • ast • enum • gettext • gzip • hashlib • importlib • importlib._abc • importlib.abc • importlib.metadata • importlib.resources._legacy • importlib.util • io • locale • logging • os • pathlib • random • re • re._parser • serial.serialposix • sre_compile • sre_constants • sre_parse • subprocess • tempfile • threading • typing • urllib.parse • zipfile

weakref SourceModule

imports: _collections_abc • _weakref • _weakrefset • atexit • copy • gc • itertools • sys

imported by: GUI_V13.py • _threading_local • copy • functools • logging • tempfile

winreg MissingModule

imported by: importlib._bootstrap_external

zipfile SourceModule

imports: argparse • binascii • bz2 • contextlib • importlib.util • io • itertools • lzma • os • pathlib • posixpath • py_compile • re • shutil • stat • struct • sys • threading • time • warnings • zlib

imported by: importlib.metadata • importlib.resources.readers • shutil

zlib (builtin module)

imported by: encodings.zlib_codec • gzip • shutil • tarfile • zipfile

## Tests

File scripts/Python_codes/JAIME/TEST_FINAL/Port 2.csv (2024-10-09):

Timestamp | Temp | Humidity | Library_Version | Session_type | Device_Number | Battery_Voltage | Motor_Turns | FR | Event | Active_Poke | Left_Poke_Count | Right_Poke_Count | Pellet_Count | Block_Pellet_Count | Retrieval_Time | InterPelletInterval | Poke_Time
2024-10-09 14:45:33.038 | 25.54 | 36.72 | 1.16.3 | FR1 | 4 | 4.19 | NaN | 1 | Right | Left | 15 | 69 | 9 | 0 | NaN | NaN | 0.10
2024-10-09 14:45:37.259 | 25.57 | 36.69 | 1.16.3 | FR1 | 4 | 4.18 | NaN | 1 | Left | Left | 16 | 69 | 9 | 0 | NaN | NaN | 0.05

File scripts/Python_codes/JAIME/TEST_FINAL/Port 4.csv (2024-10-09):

Timestamp | Temp | Humidity | Library_Version | Session_type | Device_Number | Battery_Voltage | Motor_Turns | FR | Event | Active_Poke | Left_Poke_Count | Right_Poke_Count | Pellet_Count | Block_Pellet_Count | Retrieval_Time | InterPelletInterval | Poke_Time
2024-10-09 14:45:29.095 | 25.79 | 31.45 | 1.16.3 | FR1 | 20 | 4.20 | NaN | 1 | Right | Left | 9 | 63 | 6 | 0 | NaN | NaN | 0.31

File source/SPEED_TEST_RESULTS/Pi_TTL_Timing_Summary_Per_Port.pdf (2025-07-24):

Port | Mean_DelaySD_Delay Mean_Duration SD_DurationN
Port 1 | 0.000242 8.638220520161587e-05 0.10019221739130435 9.39206418021148e-05 23
Port 2 | 0.000279 9.484677116275496e-05 0.100225 0.000197 | 25
Port 3 | 0.000308 0.00011 0.10018440740740742 9.244510190429971e-05 27
Port 4 | 0.00025 6.831735898336188e-05 0.10019253846153846 0.000103 | 26

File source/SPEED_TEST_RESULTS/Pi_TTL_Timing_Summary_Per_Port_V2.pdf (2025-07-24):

Port # | Mean delay | SD delay | Mean duration | SD duration | N
Port 1 | 0.000242391 8.638220520161587e-05 0.10019221739130435 9.39206418021148e-05 23
Port 2 | 0.00027892 9.484677116275496e-05 | 0.10022492 | 0.000196539 | 25
Port 3 | 0.000308222 | 0.000109588 | 0.10018440740740742 9.244510190429971e-05 27
Port 4 | 0.000249692 6.831735898336188e-05 0.10019253846153846 | 0.000102958 | 26

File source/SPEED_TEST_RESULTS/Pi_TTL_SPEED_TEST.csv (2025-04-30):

"2025-04-16 11:24:22: Port 2 raw data: ['4/16/2025 11:24:22', '25.86', '26.36', '1.16.3', 'FR1', '10', '4.14', 'NaN', '1', 'Right', 'Left', '8', '30', '7', '0', 'NaN', 'NaN', '0.82']"
2025-04-16 11:24:22: [2025-04-16 11:24:22.220] Port 2 - Event: Right
2025-04-16 11:24:22: TTL signal sent on Port 2 for Right
2025-04-16 11:24:22: Delay from FED3 data received to TTL start: 0.000169 seconds
2025-04-16 11:24:22: Delay from TTL start to end (GPIO toggling): 0.100089 seconds
"2025-04-16 11:24:22: Port 1 raw data: ['4/16/2025 11:24:22', '24.05', '35.60', '1.16.3', 'FR1', '14', '4.20', 'NaN', '1', 'Right', 'Left', '6', '31', '6', '0', 'NaN', 'NaN', '1.65']"
2025-04-16 11:24:22: [2025-04-16 11:24:22.866] Port 1 - Event: Right
2025-04-16 11:24:23: TTL signal sent on Port 1 for Right
2025-04-16 11:24:23: Delay from FED3 data received to TTL start: 0.000187 seconds
2025-04-16 11:24:23: Delay from TTL start to end (GPIO toggling): 0.100166 seconds
"2025-04-16 11:24:27: Port 4 raw data: ['4/16/2025 11:24:27', '23.99', '32.58', '1.16.3', 'FR1', '11', '4.20', 'NaN', '1', 'Right', 'Left', '4', '23', '4', '0', 'NaN', 'NaN', '1.09']"
2025-04-16 11:24:27: [2025-04-16 11:24:27.199] Port 4 - Event: Right
"2025-04-16 11:24:27: Port 3 raw data: ['7/11/2085 11:27:03', '24.83', '29.09', '1.16.3', 'FR1', '20', '4.20', 'NaN', '1', 'Right', 'Left', '0', '10', '0', '0', 'NaN', 'NaN', '1.29']"
2025-04-16 11:24:27: [2025-04-16 11:24:27.312] Port 3 - Event: Right
2025-04-16 11:24:27: TTL signal sent on Port 4 for Right
2025-04-16 11:24:27: Delay from FED3 data received to TTL start: 0.000363 seconds
2025-04-16 11:24:27: Delay from TTL start to end (GPIO toggling): 0.100166 seconds
2025-04-16 11:24:27: TTL signal sent on Port 3 for Right
2025-04-16 11:24:27: Delay from FED3 data received to TTL start: 0.000455 seconds
2025-04-16 11:24:27: Delay from TTL start to end (GPIO toggling): 0.100162 seconds
"2025-04-16 11:24:39: Port 1 raw data: ['4/16/2025 11:24:39', '24.08', '35.58', '1.16.3', 'FR1', '14', '4.20', 'NaN', '1', 'Right', 'Left', '6', '32', '6', '0', 'NaN', 'NaN', '0.85']"
2025-04-16 11:24:39: [2025-04-16 11:24:39.842] Port 1 - Event: Right
"2025-04-16 11:24:39: Port 2 raw data: ['4/16/2025 11:24:39', '25.88', '26.35', '1.16.3', 'FR1', '10', '4.14', 'NaN', '1', 'Right', 'Left', '8', '31', '7', '0', 'NaN', 'NaN', '0.76']"
2025-04-16 11:24:39: [2025-04-16 11:24:39.837] Port 2 - Event: Right
2025-04-16 11:24:39: TTL signal sent on Port 1 for Right
2025-04-16 11:24:39: Delay from FED3 data received to TTL start: 0.000233 seconds
2025-04-16 11:24:39: Delay from TTL start to end (GPIO toggling): 0.100229 seconds
2025-04-16 11:24:39: TTL signal sent on Port 2 for Right
2025-04-16 11:24:39: Delay from FED3 data received to TTL start: 0.000554 seconds
2025-04-16 11:24:39: Delay from TTL start to end (GPIO toggling): 0.100220 seconds
"2025-04-16 11:24:48: Port 3 raw data: ['7/11/2085 11:27:24', '24.80', '29.23', '1.16.3', 'FR1', '20', '4.20', 'NaN', '1', 'Right', 'Left', '0', '11', '0', '0', 'NaN', 'NaN', '2.19']"
2025-04-16 11:24:48: [2025-04-16 11:24:48.903] Port 3 - Event: Right
"2025-04-16 11:24:48: Port 4 raw data: ['4/16/2025 11:24:48', '23.96', '32.69', '1.16.3', 'FR1', '11', '4.20', 'NaN', '1', 'Right', 'Left', '4', '24', '4', '0', 'NaN', 'NaN', '1.47']"
2025-04-16 11:24:48: [2025-04-16 11:24:48.866] Port 4 - Event: Right
2025-04-16 11:24:49: TTL signal sent on Port 3 for Right
2025-04-16 11:24:49: Delay from FED3 data received to TTL start: 0.000241 seconds
2025-04-16 11:24:49: Delay from TTL start to end (GPIO toggling): 0.100163 seconds
2025-04-16 11:24:49: TTL signal sent on Port 4 for Right
2025-04-16 11:24:49: Delay from FED3 data received to TTL start: 0.000318 seconds
2025-04-16 11:24:49: Delay from TTL start to end (GPIO toggling): 0.100176 seconds
"2025-04-16 11:24:52: Port 1 raw data: ['4/16/2025 11:24:52', '24.07', '35.53', '1.16.3', 'FR1', '14', '4.20', 'NaN', '1', 'Right', 'Left', '6', '33', '6', '0', 'NaN', 'NaN', '0.19']"
2025-04-16 11:24:52: [2025-04-16 11:24:52.586] Port 1 - Event: Right
2025-04-16 11:24:52: TTL signal sent on Port 1 for Right
2025-04-16 11:24:52: Delay from FED3 data received to TTL start: 0.000143 seconds
2025-04-16 11:24:52: Delay from TTL start to end (GPIO toggling): 0.100127 seconds
"2025-04-16 11:24:55: Port 2 raw data: ['4/16/2025 11:24:55', '25.88', '26.38', '1.16.3', 'FR1', '10', '4.14', 'NaN', '1', 'Right', 'Left', '8', '32', '7', '0', 'NaN', 'NaN', '0.26']"
2025-04-16 11:24:55: [2025-04-16 11:24:55.294] Port 2 - Event: Right
2025-04-16 11:24:55: TTL signal sent on Port 2 for Right
2025-04-16 11:24:55: Delay from FED3 data received to TTL start: 0.000169 seconds
2025-04-16 11:24:55: Delay from TTL start to end (GPIO toggling): 0.100153 seconds
"2025-04-16 11:24:58: Port 3 raw data: ['7/11/2085 11:27:34', '24.78', '29.26', '1.16.3', 'FR1', '20', '4.20', 'NaN', '1', 'Right', 'Left', '0', '12', '0', '0', 'NaN', 'NaN', '0.45']"
2025-04-16 11:24:58: [2025-04-16 11:24:58.306] Port 3 - Event: Right
2025-04-16 11:24:58: TTL signal sent on Port 3 for Right
2025-04-16 11:24:58: Delay from FED3 data received to TTL start: 0.000358 seconds
2025-04-16 11:24:58: Delay from TTL start to end (GPIO toggling): 0.100170 seconds
"2025-04-16 11:25:01: Port 4 raw data: ['4/16/2025 11:25:01', '23.99', '32.65', '1.16.3', 'FR1', '11', '4.20', 'NaN', '1', 'Right', 'Left', '4', '25', '4', '0', 'NaN', 'NaN', '0.48']"
2025-04-16 11:25:01: [2025-04-16 11:25:01.191] Port 4 - Event: Right
2025-04-16 11:25:01: TTL signal sent on Port 4 for Right
2025-04-16 11:25:01: Delay from FED3 data received to TTL start: 0.000290 seconds
2025-04-16 11:25:01: Delay from TTL start to end (GPIO toggling): 0.100150 seconds
"2025-04-16 11:25:09: Port 4 raw data: ['4/16/2025 11:25:09', '23.98', '32.66', '1.16.3', 'FR1', '11', '4.20', 'NaN', '1', 'Right', 'Left', '4', '26', '4', '0', 'NaN', 'NaN', '0.18']"
2025-04-16 11:25:09: [2025-04-16 11:25:09.640] Port 4 - Event: Right
2025-04-16 11:25:09: TTL signal sent on Port 4 for Right
2025-04-16 11:25:09: Delay from FED3 data received to TTL start: 0.000276 seconds
2025-04-16 11:25:09: Delay from TTL start to end (GPIO toggling): 0.100623 seconds
"2025-04-16 11:25:12: Port 3 raw data: ['7/11/2085 11:27:47', '24.77', '29.24', '1.16.3', 'FR1', '20', '4.20', 'NaN', '1', 'Right', 'Left', '0', '13', '0', '0', 'NaN', 'NaN', '0.20']"
2025-04-16 11:25:12: [2025-04-16 11:25:11.936] Port 3 - Event: Right
2025-04-16 11:25:12: TTL signal sent on Port 3 for Right
2025-04-16 11:25:12: Delay from FED3 data received to TTL start: 0.000216 seconds
2025-04-16 11:25:12: Delay from TTL start to end (GPIO toggling): 0.100134 seconds
"2025-04-16 11:25:13: Port 2 raw data: ['4/16/2025 11:25:13', '25.89', '26.28', '1.16.3', 'FR1', '10', '4.14', 'NaN', '1', 'Right', 'Left', '8', '33', '7', '0', 'NaN', 'NaN', '0.10']"
2025-04-16 11:25:13: [2025-04-16 11:25:13.754] Port 2 - Event: Right
2025-04-16 11:25:13: TTL signal sent on Port 2 for Right
2025-04-16 11:25:13: Delay from FED3 data received to TTL start: 0.000261 seconds
2025-04-16 11:25:13: Delay from TTL start to end (GPIO toggling): 0.100354 seconds
"2025-04-16 11:25:15: Port 1 raw data: ['4/16/2025 11:25:15', '24.07', '35.50', '1.16.3', 'FR1', '14', '4.20', 'NaN', '1', 'Right', 'Left', '6', '34', '6', '0', 'NaN', 'NaN', '0.57']"
2025-04-16 11:25:15: [2025-04-16 11:25:15.871] Port 1 - Event: Right
2025-04-16 11:25:16: TTL signal sent on Port 1 for Right
2025-04-16 11:25:16: Delay from FED3 data received to TTL start: 0.000250 seconds
2025-04-16 11:25:16: Delay from TTL start to end (GPIO toggling): 0.100140 seconds
"2025-04-16 11:25:21: Port 1 raw data: ['4/16/2025 11:25:21', '24.07', '35.54', '1.16.3', 'FR1', '14', '4.20', 'NaN', '1', 'Left', 'Left', '7', '34', '6', '0', 'NaN', 'NaN', '0.24']"
2025-04-16 11:25:21: [2025-04-16 11:25:21.500] Port 1 - Event: Left
2025-04-16 11:25:21: TTL signal sent on Port 1 for Left
2025-04-16 11:25:21: Delay from FED3 data received to TTL start: 0.000267 seconds
2025-04-16 11:25:21: Delay from TTL start to end (GPIO toggling): 0.100224 seconds
"2025-04-16 11:25:23: Port 2 raw data: ['4/16/2025 11:25:23', '25.90', '26.34', '1.16.3', 'FR1', '10', '4.14', 'NaN', '1', 'Left', 'Left', '9', '33', '7', '0', 'NaN', 'NaN', '0.20']"
2025-04-16 11:25:23: [2025-04-16 11:25:23.199] Port 2 - Event: Left
2025-04-16 11:25:23: TTL signal sent on Port 2 for Left
2025-04-16 11:25:23: Delay from FED3 data received to TTL start: 0.000282 seconds
2025-04-16 11:25:23: Delay from TTL start to end (GPIO toggling): 0.100164 seconds
"2025-04-16 11:25:24: Port 3 raw data: ['7/11/2085 11:28:00', '24.74', '29.24', '1.16.3', 'FR1', '20', '4.19', 'NaN', '1', 'Left', 'Left', '1', '13', '0', '0', 'NaN', 'NaN', '0.27']"
2025-04-16 11:25:24: [2025-04-16 11:25:24.896] Port 3 - Event: Left
2025-04-16 11:25:25: TTL signal sent on Port 3 for Left
2025-04-16 11:25:25: Delay from FED3 data received to TTL start: 0.000373 seconds
2025-04-16 11:25:25: Delay from TTL start to end (GPIO toggling): 0.100171 seconds
"2025-04-16 11:25:26: Port 4 raw data: ['4/16/2025 11:25:26', '23.96', '32.67', '1.16.3', 'FR1', '11', '4.20', 'NaN', '1', 'Left', 'Left', '5', '26', '4', '0', 'NaN', 'NaN', '0.26']"
2025-04-16 11:25:26: [2025-04-16 11:25:26.376] Port 4 - Event: Left
2025-04-16 11:25:26: TTL signal sent on Port 4 for Left
2025-04-16 11:25:26: Delay from FED3 data received to TTL start: 0.000351 seconds
2025-04-16 11:25:26: Delay from TTL start to end (GPIO toggling): 0.100170 seconds
"2025-04-16 11:25:29: Port 4 raw data: ['4/16/2025 11:25:29', '23.95', '32.68', '1.16.3', 'FR1', '11', '4.20', 'NaN', '1', 'PelletInWell', 'Left', '5', '26', '4', '0', 'NaN', 'NaN', 'NaN']"
2025-04-16 11:25:29: [2025-04-16 11:25:29.646] Port 4 - Event: PelletInWell
"2025-04-16 11:25:29: Pellet dispensed in well, signal ON."
"2025-04-16 11:25:30: Port 4 raw data: ['4/16/2025 11:25:30', '23.98', '32.68', '1.16.3', 'FR1', '11', '4.20', '3', '1', 'Pellet', 'Left', '5', '26', '5', '0', '0.82', '289', 'NaN']"
2025-04-16 11:25:30: [2025-04-16 11:25:30.535] Port 4 - Event: Pellet
"2025-04-16 11:25:30: Pellet taken, signal turned OFF."
2025-04-16 11:25:30: TTL signal sent on Port 4 for Pellet
2025-04-16 11:25:30: Delay from FED3 data received to TTL start: 0.000274 seconds
2025-04-16 11:25:30: Delay from TTL start to end (GPIO toggling): 0.100259 seconds
"2025-04-16 11:25:32: Port 3 raw data: ['7/11/2085 11:28:08', '24.73', '29.30', '1.16.3', 'FR1', '20', '4.20', 'NaN', '1', 'PelletInWell', 'Left', '1', '13', '0', '0', 'NaN', 'NaN', 'NaN']"
2025-04-16 11:25:32: [2025-04-16 11:25:32.642] Port 3 - Event: PelletInWell
"2025-04-16 11:25:32: Pellet dispensed in well, signal ON."
"2025-04-16 11:25:33: Port 3 raw data: ['7/11/2085 11:28:09', '24.73', '29.28', '1.16.3', 'FR1', '20', '4.20', '5', '1', 'Pellet', 'Left', '1', '13', '1', '0', '0.79', 'NaN', 'NaN']"
2025-04-16 11:25:33: [2025-04-16 11:25:33.496] Port 3 - Event: Pellet
"2025-04-16 11:25:33: Pellet taken, signal turned OFF."
2025-04-16 11:25:33: TTL signal sent on Port 3 for Pellet
2025-04-16 11:25:33: Delay from FED3 data received to TTL start: 0.000282 seconds
2025-04-16 11:25:33: Delay from TTL start to end (GPIO toggling): 0.100194 seconds
"2025-04-16 11:25:34: Port 2 raw data: ['4/16/2025 11:25:34', '25.90', '26.36', '1.16.3', 'FR1', '10', '4.14', 'NaN', '1', 'PelletInWell', 'Left', '9', '33', '7', '0', 'NaN', 'NaN', 'NaN']"
2025-04-16 11:25:34: [2025-04-16 11:25:34.659] Port 2 - Event: PelletInWell
"2025-04-16 11:25:34: Pellet dispensed in well, signal ON."
"2025-04-16 11:25:35: Port 2 raw data: ['4/16/2025 11:25:35', '25.90', '26.36', '1.16.3', 'FR1', '10', '4.14', '6', '1', 'Pellet', 'Left', '9', '33', '8', '0', '0.77', '292', 'NaN']"
2025-04-16 11:25:35: [2025-04-16 11:25:35.489] Port 2 - Event: Pellet
"2025-04-16 11:25:35: Pellet taken, signal turned OFF."
2025-04-16 11:25:35: TTL signal sent on Port 2 for Pellet
2025-04-16 11:25:35: Delay from FED3 data received to TTL start: 0.000400 seconds
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

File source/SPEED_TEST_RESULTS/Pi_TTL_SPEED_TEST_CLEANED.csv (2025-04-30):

Port | Event | Delay_to_TTL_Start_sec | TTL_Duration_sec
Port 2 | Right | 0.000169 | 0.100089
Port 1 | Right | 0.000187 | 0.100166
Port 3 | Right | 0.000363 | 0.100166
Port 3 | Right | 0.000455 | 0.100162
Port 2 | Right | 0.000233 | 0.100229
Port 2 | Right | 0.000554 | 0.10022
Port 4 | Right | 0.000241 | 0.100163
Port 4 | Right | 0.000318 | 0.100176
Port 1 | Right | 0.000143 | 0.100127
Port 2 | Right | 0.000169 | 0.100153
Port 3 | Right | 0.000358 | 0.10017
Port 4 | Right | 0.00029 | 0.10015
Port 4 | Right | 0.000276 | 0.100623
Port 3 | Right | 0.000216 | 0.100134
Port 2 | Right | 0.000261 | 0.100354
Port 1 | Right | 0.00025 | 0.10014
Port 1 | Left | 0.000267 | 0.100224
Port 2 | Left | 0.000282 | 0.100164
Port 3 | Left | 0.000373 | 0.100171
Port 4 | Left | 0.000351 | 0.10017
Port 4 | Pellet | 0.000274 | 0.100259
Port 3 | Pellet | 0.000282 | 0.100194
Port 2 | Pellet | 0.0004 | 0.100172
Port 1 | Pellet | 0.000324 | 0.100207
Port 2 | Left | 0.000139 | 0.100115
Port 1 | Left | 0.000314 | 0.100144
Port 4 | Left | 0.000188 | 0.100192
Port 3 | Left | 0.000317 | 0.100134
Port 1 | Pellet | 0.000166 | 0.100115
Port 2 | Pellet | 0.000344 | 0.100186
Port 3 | Pellet | 0.000158 | 0.100123
Port 4 | Pellet | 0.00026 | 0.100124
Port 1 | Right | 0.000276 | 0.100178
Port 3 | Right | 0.000299 | 0.100152
Port 4 | Right | 0.000218 | 0.100186
Port 2 | Right | 0.000341 | 0.100153
Port 4 | Right | 0.000139 | 0.100128
Port 4 | Right | 6.9e-05 | 0.100108
Port 1 | Right | 0.000265 | 0.100118
Port 3 | Right | 0.000513 | 0.100154
Port 4 | Left | 0.000281 | 0.100156
Port 1 | Left | 0.000286 | 0.100165
Port 3 | Left | 0.000269 | 0.100142
Port 3 | Left | 0.000385 | 0.100437
Port 4 | Pellet | 0.00033 | 0.100186
Port 3 | Pellet | 0.00048 | 0.10014
Port 2 | Pellet | 0.000318 | 0.100143
Port 1 | RightWithPellet | 0.000153 | 0.100126
Port 1 | LeftWithPellet | 0.000138 | 0.100145
Port 1 | RightWithPellet | 0.000356 | 0.100148
Port 1 | LeftWithPellet | 0.000239 | 0.100121
Port 1 | Pellet | 0.000156 | 0.100326
Port 2 | Left | 0.000273 | 0.100173
Port 2 | RightWithPellet | 0.000268 | 0.100725
Port 2 | LeftWithPellet | 0.000271 | 0.100164
Port 2 | RightWithPellet | 0.000356 | 0.100165
Port 2 | LeftWithPellet | 0.000209 | 0.100213
Port 2 | Pellet | 0.00016 | 0.100965
Port 3 | Left | 0.000215 | 0.100105
Port 3 | RightWithPellet | 0.000138 | 0.100134
Port 3 | LeftWithPellet | 0.000256 | 0.100201
Port 3 | RightWithPellet | 0.000287 | 0.100124
Port 3 | LeftWithPellet | 0.000538 | 0.100152
Port 3 | Pellet | 0.000432 | 0.100131
Port 4 | Left | 0.000281 | 0.100158
Port 4 | RightWithPellet | 0.000283 | 0.100162
Port 4 | LeftWithPellet | 0.000272 | 0.100214
Port 4 | LeftWithPellet | 0.000283 | 0.100389
Port 4 | RightWithPellet | 0.00022 | 0.100117
Port 4 | Pellet | 0.000304 | 0.100164
Port 1 | Right | 0.000266 | 0.100218
Port 2 | Right | 0.000258 | 0.10012
Port 3 | Right | 0.000269 | 0.100283
Port 4 | Right | 0.000288 | 0.100177
Port 4 | Right | 0.000287 | 0.100155
Port 3 | Right | 0.000271 | 0.100176
Port 2 | Right | 0.000258 | 0.100142
Port 1 | Right | 0.000152 | 0.100126
Port 1 | Right | 0.000259 | 0.100299
Port 1 | Right | 0.000506 | 0.100166
Port 2 | Right | 0.000298 | 0.100157
Port 3 | Right | 0.000321 | 0.100175
Port 2 | Right | 0.00027 | 0.100202
Port 3 | Right | 0.000353 | 0.100161
Port 4 | Right | 0.000268 | 0.100154
Port 4 | Right | 0.000171 | 0.100179
Port 1 | Left | 0.000164 | 0.10021
Port 2 | Left | 0.000276 | 0.100132
Port 3 | Left | 0.000243 | 0.100152
Port 4 | Left | 0.000307 | 0.100196
Port 1 | LeftWithPellet | 0.000249 | 0.100161
Port 1 | LeftWithPellet | 0.00028 | 0.100533
Port 1 | Pellet | 0.000179 | 0.100258
Port 2 | LeftWithPellet | 0.000145 | 0.10012
Port 2 | RightWithPellet | 0.000283 | 0.100165
Port 2 | Pellet | 0.000438 | 0.100202
Port 3 | LeftWithPellet | 0.000178 | 0.100181
Port 3 | RightWithPellet | 0.000165 | 0.100522
Port 3 | Pellet | 0.000188 | 0.100203
Port 4 | LeftWithPellet | 0.00015 | 0.100135
Port 4 | RightWithPellet | 0.000143 | 0.100185

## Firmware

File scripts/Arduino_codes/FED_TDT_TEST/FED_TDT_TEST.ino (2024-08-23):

//////////////// Here I am just testing the output using LED
//int pulsePin = 10; // Use pin 10 for the LED or pulse output
//
//void setup() {
//  Serial.begin(115200);
//  pinMode(pulsePin, OUTPUT); // Set pin 10 as an output
//}
//
//void loop() {
//  if (Serial.available() > 0) {
//    String data = Serial.readStringUntil('\n');
//    
//    // Generate a pulse when data is received
//    digitalWrite(pulsePin, HIGH);  // Turn the LED on or send a pulse
//    delay(10);                     // 10 ms pulse duration
//    digitalWrite(pulsePin, LOW);   // Turn the LED off or end the pulse
//    
//    Serial.print("Received: ");
//    Serial.println(data);  // Print the received data to the Serial Monitor
//  }
//}

/////////////////////////////////////////////////////////////////////////////////////
/////////////////////////////////////////////////////////////////////

//same code just different documentation 

//int pulsePin = 10; // Digital pin for output pulse to TDT
//
//void setup() {
//  Serial.begin(115200); // Initialize serial communication at 115200 baud rate
//  pinMode(pulsePin, OUTPUT); // Set pin 10 as an output for the pulse
//}
//
//void loop() {
//  if (Serial.available() > 0) { 
//    // Check if data is available to read from the serial port
//    char incomingByte = Serial.read(); // Read the incoming byte
//    
//    // Generate a pulse on pin 10 to send a signal to the TDT system
//    digitalWrite(pulsePin, HIGH);  // Send a HIGH signal (pulse) to TDT
//    delay(10);                     // 10 ms pulse duration (adjust if needed)
//    digitalWrite(pulsePin, LOW);   // End the pulse (set pin 10 to LOW)
//
//    // (Optional) Print the received byte for debugging
//    Serial.print("Received: ");
//    Serial.println(incomingByte);
//  }
//}


///////////////////////////////
//we can try this code to send distinct TTLs to TDT
//int pulsePin = 10; // Pin for output pulse
//
//void setup() {
//  Serial.begin(115200);
//  pinMode(pulsePin, OUTPUT); // Set pin 10 as an output
//}
//
//void loop() {
//  if (Serial.available() > 0) {
//    char eventType = Serial.read(); // Read the event type identifier
//
//    switch(eventType) {
//      case 'R': // Right poke event
//        generatePulse(1); // Single pulse
//        break;
//      case 'L': // Left poke event
//        generatePulse(2); // Double pulse
//        break;
//      case 'P': // Pellet intake event
//        generatePulse(3); // Triple pulse
//        break;
//      case 'W': // Left with pellet event
//        generatePulse(4); // Quadruple pulse
//        break;
//      case 'Q': // Right with pellet event
//        generatePulse(5); // Quintuple pulse
//        break;
//    }
//  }
//}
//
//void generatePulse(int pulseCount) {
//  for (int i = 0; i < pulseCount; i++) {
//    digitalWrite(pulsePin, HIGH);  // Send a pulse
//    delay(10);                     // 10 ms pulse duration
//    digitalWrite(pulsePin, LOW);   // End the pulse
//    delay(100);                    // Wait 100 ms between pulses
//  }
//}
//

///////////////////////////
//here trying to send different TTL signals through separate pins for each behavioural event
//int leftPokePin = 9;           // Pin for left poke event
//int leftWithPelletPin = 10;    // Pin for left poke with pellet event
//int rightPokePin = 11;         // Pin for right poke event
//int rightWithPelletPin = 12;   // Pin for right poke with pellet event
//int pelletIntakePin = 13;      // Pin for pellet intake event
//
//void setup() {
//  Serial.begin(115200);
//  pinMode(leftPokePin, OUTPUT);         // Set pin 9 as an output
//  pinMode(leftWithPelletPin, OUTPUT);   // Set pin 10 as an output
//  pinMode(rightPokePin, OUTPUT);        // Set pin 11 as an output
//  pinMode(rightWithPelletPin, OUTPUT);  // Set pin 12 as an output
//  pinMode(pelletIntakePin, OUTPUT);     // Set pin 13 as an output
//}
//void loop() {
//  if (Serial.available() > 0) {
//    char eventType = Serial.read(); // Read the event type identifier
//    Serial.print("Received event type: ");
//    Serial.println(eventType); // Print the received event type for debugging
//
//    switch(eventType) {
//      case 'l': // Left poke event
//        Serial.println("Triggering left poke pin (9)");
//        generatePulse(leftPokePin);   // Send pulse on left poke pin
//        break;
//      case 'w': // Left with pellet event
//        Serial.println("Triggering left with pellet pin (10)");
//        generatePulse(leftWithPelletPin); // Send pulse on left with pellet pin
//        break;
//      case 'r': // Right poke event
//        Serial.println("Triggering right poke pin (11)");
//        generatePulse(rightPokePin);  // Send pulse on right poke pin
//        break;
//      case 'q': // Right with pellet event
//        Serial.println("Triggering right with pellet pin (12)");
//        generatePulse(rightWithPelletPin); // Send pulse on right with pellet pin
//        break;
//      case 'p': // Pellet intake event
//        Serial.println("Triggering pellet intake pin (13)");
//        generatePulse(pelletIntakePin);  // Send pulse on pellet intake pin
//        break;
//      default:
//        Serial.println("Unknown event type received.");
//        break;
//    }
//  }
//}
//
//
//void generatePulse(int pin) {
//  digitalWrite(pin, HIGH);  // Send a pulse
//  delay(10);                // 10 ms pulse duration
//  digitalWrite(pin, LOW);   // End the pulse
//}
//
//

/////
///Testing LED functions and making sure Python interacts correctly
//int leftPokePin = 9;           // Pin for left poke event
//int rightPokePin = 11;         // Pin for right poke event
//int pelletIntakePin = 13;      // Pin for pellet intake event
//
//void setup() {
//  Serial.begin(115200);
//  pinMode(leftPokePin, OUTPUT);         
//  pinMode(rightPokePin, OUTPUT);        
//  pinMode(pelletIntakePin, OUTPUT);     
//}
//
//void loop() {
//  if (Serial.available() > 0) {
//    char eventType = Serial.read(); // Read the event type identifier
//    Serial.print("Received event type: ");
//    Serial.println(eventType); // Print the received event type for debugging
//
//    if (eventType == 'L') {
//        digitalWrite(leftPokePin, HIGH);   // Turn on left poke LED
//        delay(1000);                       // Keep it on for 1 second
//        digitalWrite(leftPokePin, LOW);    // Turn it off
//        Serial.println("Left poke LED triggered");
//    } 
//    else if (eventType == 'R') {
//        digitalWrite(rightPokePin, HIGH);  // Turn on right poke LED
//        delay(1000);                       // Keep it on for 1 second
//        digitalWrite(rightPokePin, LOW);   // Turn it off
//        Serial.println("Right poke LED triggered");
//    } 
//    else if (eventType == 'P') {
//        digitalWrite(pelletIntakePin, HIGH);  // Turn on pellet intake LED
//        delay(1000);                          // Keep it on for 1 second
//        digitalWrite(pelletIntakePin, LOW);   // Turn it off
//        Serial.println("Pellet intake LED triggered");
//    }
//  }
//}

/////////////////////////////////////////////////////Here the latest code////////////////////////////////////

//int leftPokePin = 9;           // Pin for left poke event
//int leftWithPelletPin = 10;    // Pin for left poke with pellet event
//int rightPokePin = 11;         // Pin for right poke event
//int rightWithPelletPin = 12;   // Pin for right poke with pellet event
//int pelletIntakePin = 13;      // Pin for pellet intake event
//
//void setup() {
//  Serial.begin(115200);
//  pinMode(leftPokePin, OUTPUT);         
//  pinMode(leftWithPelletPin, OUTPUT);   
//  pinMode(rightPokePin, OUTPUT);        
//  pinMode(rightWithPelletPin, OUTPUT);  
//  pinMode(pelletIntakePin, OUTPUT);     
//}
//
//void loop() {
//  if (Serial.available() > 0) {
//    char eventType = Serial.read(); // Read the event type identifier
//    Serial.print("Received event type: ");
//    Serial.println(eventType); // Print the received event type for debugging
//
//    if (eventType == 'L') {
//        digitalWrite(leftPokePin, HIGH);   // Turn on left poke LED
//        delay(1000);                       // Keep it on for 1 second
//        digitalWrite(leftPokePin, LOW);    // Turn it off
//        Serial.println("Left poke LED triggered");
//    } 
//    else if (eventType == 'W') {
//        digitalWrite(leftWithPelletPin, HIGH);  // Turn on left with pellet LED
//        delay(1000);                            // Keep it on for 1 second
//        digitalWrite(leftWithPelletPin, LOW);   // Turn it off
//        Serial.println("Left with pellet LED triggered");
//    } 
//    else if (eventType == 'R') {
//        digitalWrite(rightPokePin, HIGH);  // Turn on right poke LED
//        delay(1000);                       // Keep it on for 1 second
//        digitalWrite(rightPokePin, LOW);   // Turn it off
//        Serial.println("Right poke LED triggered");
//    } 
//    else if (eventType == 'Q') {
//        digitalWrite(rightWithPelletPin, HIGH);  // Turn on right with pellet LED
//        delay(1000);                             // Keep it on for 1 second
//        digitalWrite(rightWithPelletPin, LOW);   // Turn it off
//        Serial.println("Right with pellet LED triggered");
//    }
//    else if (eventType == 'P') {
//        digitalWrite(pelletIntakePin, HIGH);  // Turn on pellet intake LED
//        delay(1000);                          // Keep it on for 1 second
//        digitalWrite(pelletIntakePin, LOW);   // Turn it off
//        Serial.println("Pellet intake LED triggered");
//    }
//  }
//}



/////////////////////////Pellet_in_well_signal////////////////////
int leftPokePin = 9;           // Pin for left poke event
int leftWithPelletPin = 10;    // Pin for left poke with pellet event
int rightPokePin = 11;         // Pin for right poke event
int rightWithPelletPin = 12;   // Pin for right poke with pellet event
int pelletPin = 13;            // Pin for both pellet in well and pellet intake events

bool pelletInWell = false;  // State variable to track if pellet is in the well

void setup() {
  Serial.begin(115200);

  // Setup pins as outputs
  pinMode(leftPokePin, OUTPUT);         
  pinMode(leftWithPelletPin, OUTPUT);   
  pinMode(rightPokePin, OUTPUT);        
  pinMode(rightWithPelletPin, OUTPUT);  
  pinMode(pelletPin, OUTPUT);     

  // Ensure all pins start LOW
  digitalWrite(leftPokePin, LOW);
  digitalWrite(leftWithPelletPin, LOW);
  digitalWrite(rightPokePin, LOW);
  digitalWrite(rightWithPelletPin, LOW);
  digitalWrite(pelletPin, LOW);
}
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

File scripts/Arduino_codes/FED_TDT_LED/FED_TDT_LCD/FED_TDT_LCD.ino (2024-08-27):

#include <LiquidCrystal.h>

// Initialize the library with the new pin numbers
LiquidCrystal lcd(2, 3, 4, 5, 6, A0);

int leftPokePin = 9;           // Pin for left poke event
int leftWithPelletPin = 10;    // Pin for left poke with pellet event
int rightPokePin = 11;         // Pin for right poke event
int rightWithPelletPin = 12;   // Pin for right poke with pellet event
int pelletPin = 13;            // Pin for both pellet in well and pellet intake events

bool pelletInWell = false;  // State variable to track if pellet is in the well

void setup() {
  Serial.begin(115200);

  // Setup pins as outputs
  pinMode(leftPokePin, OUTPUT);         
  pinMode(leftWithPelletPin, OUTPUT);   
  pinMode(rightPokePin, OUTPUT);        
  pinMode(rightWithPelletPin, OUTPUT);  
  pinMode(pelletPin, OUTPUT);     

  // Ensure all pins start LOW
  digitalWrite(leftPokePin, LOW);
  digitalWrite(leftWithPelletPin, LOW);
  digitalWrite(rightPokePin, LOW);
  digitalWrite(rightWithPelletPin, LOW);
  digitalWrite(pelletPin, LOW);

// Initialize the LCD
lcd.begin(16, 2);

// Convert the message to a String object
String message = "...McCutcheonLab Technologies...";

// Scroll the welcome message
for (int i = 0; i < message.length() - 15; i++) {  // message.length() - 15 ensures we stop scrolling when there's no more to display
  lcd.clear();
  lcd.setCursor(0, 0);
  lcd.print(message.substring(i, i + 16));  // Display a substring of the message
  delay(300);  // Adjust delay as needed for smoother scrolling
}

// Clear the display after scrolling completes
lcd.clear();
delay(500);  // Pause briefly before showing the next message

// Display the second message
lcd.setCursor(0, 0); // Move to the first line
lcd.print("System Ready!");
delay(3000); // Show the message for 3 seconds
lcd.clear();

}

void loop() {
  if (Serial.available() > 0) {
    char eventType = Serial.read(); // Read the event type identifier
    Serial.print("Received event type: ");
    Serial.println(eventType); // Print the received event type for debugging

    lcd.clear(); // Clear the previous message
    lcd.print("Event: "); // Start with "Event: "

    switch (eventType) {
      case 'L': // Left poke event
        digitalWrite(leftPokePin, HIGH);
        delay(10);
        digitalWrite(leftPokePin, LOW);
        Serial.println("Left poke LED triggered");
        lcd.setCursor(0, 1); // Move to the second line
        lcd.print("Left Poke");
        break;

      case 'W': // Left with pellet event
        digitalWrite(leftWithPelletPin, HIGH);
        delay(10);
        digitalWrite(leftWithPelletPin, LOW);
        Serial.println("Left with pellet LED triggered");
        lcd.setCursor(0, 1);
        lcd.print("Left + Pellet");
        break;

      case 'R': // Right poke event
        digitalWrite(rightPokePin, HIGH);
        delay(10);
        digitalWrite(rightPokePin, LOW);
        Serial.println("Right poke LED triggered");
        lcd.setCursor(0, 1);
        lcd.print("Right Poke");
        break;

      case 'Q': // Right with pellet event
        digitalWrite(rightWithPelletPin, HIGH);
        delay(10);
        digitalWrite(rightWithPelletPin, LOW);
        Serial.println("Right with pellet LED triggered");
        lcd.setCursor(0, 1);
        lcd.print("Right + Pellet");
        break;

      case 'P': // Pellet in well or pellet intake event
        if (pelletInWell) {
          // Pellet is taken
          digitalWrite(pelletPin, LOW);   // Turn off the signal briefly
          delay(10);                      // Short delay
          pelletInWell = false;           // Update state
          Serial.println("Pellet taken: Signal turned OFF briefly");
          lcd.setCursor(0, 1);
          lcd.print("Pellet Taken");
        } else {
          // Pellet is in the well
          digitalWrite(pelletPin, HIGH);  // Keep the signal on
          pelletInWell = true;            // Update state
          Serial.println("Pellet in well: Signal turned ON");
          lcd.setCursor(0, 1);
          lcd.print("Pellet in Well");
        }
        break;

      default:
        Serial.println("Unknown event type received");
        lcd.setCursor(0, 1);
        lcd.print("Unknown Event");
        break;
    }
  }
}

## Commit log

2024-08-07 FED3_lib_update
    updated the library .scr of FED3 to generate a sound alarm instead of blinking LED
2024-08-07 python_script_serial_monitor
    created a python script to read the serial monitor output and save it as a csv file
    [COM16_log.csv]
2024-08-08 Google_spread_sheet
    made API with credentials to enable the python script to read the data of FED and log it online
    [COM16_log.csv]
2024-08-08 multiple_fed_sheets
    I developed the code to get the data from multiple FEDs and store them on a single Google Sheet but on different worksheets according to the port number
    [COM12_log.csv, COM16_log.csv]
2024-08-09 JAM_EMAIL
    generated a short script that can be used in Apps Script in Google to send an alarm email to the user whenever the device is Jammed
2024-08-21 Arduino_connected
    flashed the arduino uno board withe code to receive signal from FED and transmit it to TDT (in progress)
2024-08-23 Arduino_FED_TDT_EVEN_TTL
    developed the code to get separate TTL signals for each behavioural event from different output pin on Arduino
2024-08-23 Pelle_In_Well_signal
    An update to FED3 library and then the arduino and python code to enable the FED to log PelletInWell instead of just pellet intake and additionally , Arduino sends a signal via the same pin for Pelle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
2025-05-15 ALL_GUIs_UPDATED
    All GUIs of RTFED are updated with lates features as of May 2025, including Device Identification, Clock Sync and Mode Selection functions
